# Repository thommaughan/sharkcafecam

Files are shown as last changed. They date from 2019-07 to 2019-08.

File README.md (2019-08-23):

# sharkcafecam
SharkCafe Cam - white shark camera tag with behavior detection triggered video

### How to navigate this repository
First of all, welcome to Shark Cafe Camera. The first thing that you will need to review is the "ToolList.md" file. This will provide you with the necessary tools and optional tools that will assist you with completing this project. Each tool is listed as the name of the tool, cost, and a blue hyperlink text which will take you the the website to order that tool. Tools that are listed as optional are not necessary for the project but can provide some ease with certain aspects. The tools listed as none optional were chosen as ideal due to the fact that you can go to your local hardware store and purchase these tools and they are the relatively cheaper versions. These are not the specific tools we used for this project but are merely recommendations. Feel free to find, borrow, or use other tools that will accomplish the same tasks.

The next step if you are not familiar with soldering should be to review the "SolderingBasics.md". This will provide you a brief overview of soldering tools and techniques that will assist you with this project. Feel free to also research other resources for example you tube videos or manuals as these can provide more detailed information about this topic.

After you have completed the first two sections or you are familiar with soldering then you are ready to navigation the rest of this repository. The organization of this reprository is as follows. Each folder describes a certain component of the overall project. The subfolders within each of these folders has  a combination of subfolder including a readme.md, mechanical, electrical, and software. First, you should open the "readme.md" which provides necessary information or steps for that component. The Mechanical describes any physical component or mechanism for that component. The electrical describes the components used and how the were wired. The software describes any software that was used to control the electrical components. 

Use these materials as guidelines to further experiment with other cameras or devices. This is merely to show how this project was accomplished and the potential possibilities. 

If you have any questions or any part of these materials are confusion, please feel free to leave comments on sections that are confusing. 

Have fun and go exploring with your new remote sensing camera!

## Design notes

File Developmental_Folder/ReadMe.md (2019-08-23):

## Developmental Files for Repository

This folder stores the necessary developmental files for this repository. These are files used in other parts of the respository for examples pictures used in the SolderingBasics Tutorial.

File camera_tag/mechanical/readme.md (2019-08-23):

## Camera Housing

  The files associated with the mechanical describe the camera housing with use of the HDR-AZ1 Sony Action camera which is unfortunately no longer in production. The "A-201898-17.PDF" shows the whole assembly with the sony cammera and batteries in place.
  "P-201897-17_SonyMold" files show the PDF view of the 3-D printed assembly housing the camera and the batteries. The other files by the same name are SolidWork files and Projects. "P-201900-17_AcrylicLens" files which were custom machined on site at the Monterey Bay Aquarium Research Institute (Double Check this).
  The "Sony Batteries" are solidworks drawings and files used with association of the "A-201898-17.PDF" as visual indicators of how the batteries are positioned in the housing. 

## How to use these files

As stated before, these files were created using the Solid Works Software which is linked below. This is a professional software platform that is used widely in many industries. A key take away from these files are to have a visual of how this version of this shark cafe camera was assembled. If you have 3-D manipulation/drafting experience, feel free use these files to create your own housing. 

[Solid Works Software](https://www.solidworks.com)

Below is a link to a 3D printing services. This is merely an example of one company. The parts for the camera housing were printed in house at the Monterey Bay Aquarium Research Institute. Use this link below as merely an example of the 3D printing services and research other alternatives if you decide to use this model. 

[3 Space Printing Service](https://3space.com/3d-printing-ppc?gclid=CjwKCAjw1_PqBRBIEiwA71rmte2ELk5xJ86E6CFk6ArePkv97ztjzFWGFQ25XP00T4se_XzOaefN1xoC2_sQAvD_BwE)

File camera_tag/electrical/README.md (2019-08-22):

# Shark Cafe Cam Main Board Information
## Files
#### 1. Schematic
#### 2. Board design
## Internal components

#### 1. Processor
#### 2. Sensors  
   Note: We show breakout boards for the sensors to show that these can be bought seperately, utilized individually, and have code and tutrials available by their manufacturers online. On the board these sensors are cut down to the essentials to make for a more compact design.
#### 3. Camera trigger
```
Note on camera trigger transistors: they allow for switching the camera on/off and record/stop. These transistors work by allowing current to flow through the camera when they are triggered. In a way they act as an electrical switch, when power is sent to them you're flipping the switch 'on', thus activating the camera, when no power is sent, the switch is flipped 'off' and the camera disactivates.
```

### Processor

| Part         | Function          | Board Code    | Description       | Link and part number      |
| --------------------|:-------------:|:-------------:|-----------------|----------------- |
|  | Processor | N/A | Central processing. Same processor found in Feather M0, can be accessed as such through Arduino IDE.| ATSAMD21G18A |

boardforedit

### Sensors (included)

| Part breakout board         | Function          | Board Code    | Description       | Link and part number      |
| --------------------|:-------------:|:-------------:|-----------------|:---------------------------:|
|   | RGB sensor  | U1  | Red, green, blue light sensor  |  [ISL29125](https://www.sparkfun.com/products/12829)   |
|   | IMU        | U4           | Accelerometer, gyroscope, and compass | [MPU-9250](https://www.invensense.com/products/motion-tracking/9-axis/mpu-9250/)   |
|   | Capacitive sensing         |   U6   | 4 Channel Capacitance to Digital Converter  | [FDC1004](http://www.ti.com/product/FDC1004)  |

### Trigger (for camera or other device. Transistor.)

| Location on board         | Function          | Board Code    | Description       | Link and part number      |
| --------------------|:-------------:| -------------|-----------------|---------------------------|
| Cam Trigger  |  2 FETs, one turns the camera on/off and the other records/stops.  | CAM1  | Trigger for camera. R and P are transistor drains, G is the common source.  |  [Transistors](https://learn.sparkfun.com/tutorials/transistors/all#extending-the-water-analogy)   |

### Electrical components

| Part Number/Name         | Function          | Board Code    | Description       | Link       |
|:--------------------:|:-------------:|:-------------:|:-----------------:|:-----------------:|
| SN74LVC2G66DCUR  | Switch         | U5    | Dual Bilateral Analog Switch  | [SN74LVC2G66DCUR](http://www.ti.com/lit/ds/symlink/sn74lvc2g66.pdf)  |
| TPS22918            | Load Switch         | U8     | Details in datasheet  | [TPS22918](http://www.ti.com/product/TPS22918)  |
| 2N7002BKS           | MOSFET         | Q1     | Transistor drain  | [2N7002BKS](https://assets.nexperia.com/documents/data-sheet/2N7002BKS.pdf)  |
| ZXCT1109            | Current sense monitor         |   U9   | Details in datasheet  | [ZXCT1109](https://www.diodes.com/assets/Datasheets/ZXCT1107_10.pdf)  |
| TPS78033            | LDO regulator         | U7     | Details in datasheet  | [TPS78033](https://www.findchips.com/detail/tps78033/2477-Texas%20Instruments?quantity=1)  |
| MCP73831            | Charge Management controller         |  U3    | Details in datasheet  | [MCP73831](https://cdn.sparkfun.com/assets/learn_tutorials/6/9/5/MCP738312.pdf)  |
| Direct wire uSD connect        | Micro SD card connector         |   J9   | Pins for soldering MicroSD card on.  | N/A  |
| USB-MICROB 5v                | Data transfer and power with computer         | J6     | Micro USB connector port  | N/A  |
   
 ### *For information on how to communicate with the board and each sensor, check out the software section.*

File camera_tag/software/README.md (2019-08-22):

For what's available on the board, navigate to [**camera_tag/electrical**](https://github.com/thommaughan/sharkcafecam/tree/master/camera_tag/electrical).

To get started with coding, head to [**software/Getting_started(+how_to_program)**](https://github.com/thommaughan/sharkcafecam/blob/master/camera_tag/software/Getting_started(%2Bhow_to_program).md).

boardforedit  
The purpose of using the same processor as the Feather M0 is so that you can communicate with this board through the Arduino IDE as you would with the M0. In other words, installing the drivers for the M0 will allow you to communicate with the main board for the camera tag.

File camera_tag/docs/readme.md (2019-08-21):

## READ ME

Each of these subfolders contains different aspects of this particular component. In this case, these folders relate to the camera, the board controlling the camera and sensor components, and the housing which contains all of these aspects. Please read each "readme" file to understand in more detail the types of files and their purpose. 

In the electrical file, there is a list of the sensor that are embedded in the board and what their function is. This also contains the layout of the board and design files. 

The mechanical file contains files related to the 3-D printed housing. 

Software contains some example codes that control different sensors of the board.

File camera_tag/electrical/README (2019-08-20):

# Shark Cafe Cam Main Board Information
## Index
1. Schematic
2. Board design
#### Internal
1. Processor
2. Sensors
| Part Number   | Name          | Board Code    | Description       |
| ------------- |:-------------:| -------------:|----------------:  |
| ISL29125            | Record        | D4_IO_PWR     | Transistor drain  |
| MPU-9250             | Ground        | N/A           | Transistor Source |
| FDC1004             | Power         | D9_IO_REC     | Transistor drain  |
| SN74             | Power         | D9_IO_REC     | Transistor drain  |
| FDC1004             | Power         | D9_IO_REC     | Transistor drain  |
| FDC1004             | Power         | D9_IO_REC     | Transistor drain  |
| FDC1004             | Power         | D9_IO_REC     | Transistor drain  |
| FDC1004             | Power         | D9_IO_REC     | Transistor drain  |
   
 For information on how to communicate with the board and each sensor, check out the software section

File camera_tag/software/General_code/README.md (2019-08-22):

### This sketch (Arduino program) contains tidbits of code for a variety of board uses.  

**Note:** Make sure to either download the necessary libraries (anything that says **#include <libraryname.h>**) or comment them out (add **//** before).  

**Note:** a piece of code needs to be added to the SD card reading lines so that the information syncs or writes. As is, empty files are being written to the SD card and once that number reaches 100 the code will stop working. ALternatively, comment out that portion.

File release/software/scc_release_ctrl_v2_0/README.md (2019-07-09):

msp430_i2cEEPROM
================

Skeleton framework for reading and writing from a  24AAxx I2C EEPROM chip for MSP430 Launchpad/MSP430g2553

Pinout for the launchpad - P1.6 = SCL; P1.7 = SDA

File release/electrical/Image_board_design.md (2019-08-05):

Board Design
-------------

<p align = 'center'>Designed by Thom Maughan</p>
<p align = 'center'><i>Eagle</i> file can be found within <b>scc_release_v2_3.zip</b></p>

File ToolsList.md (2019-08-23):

## Tools List

1. Aven Soldering/Desoldering kit: $29.52 - [Soldering Iron Kit: HomeDepot](https://www.homedepot.com/p/Aven-Soldering-Desoldering-Kit-7-Piece-17502/206311913)
2. Precision Wire Strippers AWG 20-10: $4.72 - [Wire Stripper: HomeDepot](https://www.homedepot.com/p/Pro-sKit-Precision-Wire-Stripper-AWG-20-10-CP-302G/206679687)
3. 28AWG Stranded Wire Kit: $14.99 - [Hook Up Wire: Amazaon](https://www.amazon.com/Electrical-different-Insulated-Temperature-Resistance/dp/B07G2HFCS1/ref=asc_df_B07G2HFCS1/?tag=hyprod-20&linkCode=df0&hvadid=242022044358&hvpos=1o2&hvnetw=g&hvrand=15746777807985423264&hvpone=&hvptwo=&hvqmt=&hvdev=c&hvdvcmdl=&hvlocint=&hvlocphy=9032735&hvtargid=aud-801381245258:pla-522539120773&psc=1)
4. (Optional) 3.5in. 2X Helping Hand with Magnifer: $12.52 - [Helping Hand Stand: HomeDepot](https://www.homedepot.com/p/Stalwart-3-5-in-2X-Helping-Hand-Magnifier-with-Stand-75-KS508/206362835
5. (Optional) High Temp Hot Glue Gun: $5.99 - [Hot Glue Gun: Amazon](https://www.amazon.com/Electrical-different-Insulated-Temperature-Resistance/dp/B07G2HFCS1/ref=asc_df_B07G2HFCS1/?tag=hyprod-20&linkCode=df0&hvadid=242022044358&hvpos=1o2&hvnetw=g&hvrand=15746777807985423264&hvpone=&hvptwo=&hvqmt=&hvdev=c&hvdvcmdl=&hvlocint=&hvlocphy=9032735&hvtargid=aud-801381245258:pla-522539120773&psc=1)

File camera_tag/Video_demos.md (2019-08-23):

Youtube demonstrations of the camera tag in action
==================================

### Youtube video of the camera tag being triggered to turn on and record by the onboard inertial measurement unit.
IMU_triggering (https://www.youtube.com/watch?v=_-qGrMnmp10&feature=youtu.be)

https://www.youtube.com/watch?v=_-qGrMnmp10&feature=youtu.be

### Youtube video of a camera being triggered to turn on using the red-green-blue light sensor on the main board.
RGB_triggering (https://www.youtube.com/watch?v=f3s8aPaXeHw&feature=youtu.be)

https://www.youtube.com/watch?v=f3s8aPaXeHw

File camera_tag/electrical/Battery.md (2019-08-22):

How to prepare a battery for your board
=========================================

*The brown cable in this setup is ground*


*Make sure the positive and negative terminals of your battery are connected to the white connecter in line with how the board's positive and negative terminal are aligned. We had to switch the wires on the battery. To do this, follow this simple guide:*
HTB1UNq4OXXXXXbNXpXXq6xXFXXXk



When connecting a battery make sure the wires are in the correct orientation within their housing. Make sure you connect the ground wire to the ground pin and the power wire to the power pin on the battery, reference the board design file to make sure.

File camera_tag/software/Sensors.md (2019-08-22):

# Access sensors on the board
In an effort to teach you how to access *any* sensor on the board, we will offer detailed instructions for a simple sensor and a more complex one. For the rest, the part number and library will be provided. The idea is that you'll follow the same procedure with the rest of the sensors as you did with the two provided. The purpose of this is to get you comfortable with navigating the code necessary to utilize these sensors in any way you please. If you already feel comfortable navigating code, feel free to download the sample code directly (camera_tag/software/sample_code).  

Sensor Libraries  
To facilitate communication with a sensor you can download a library.
```
Note: A library is a compilation of functions for a specific module or sensor. It allows for facilitated control of a device by offering the code to control it in more easily understood snippets. You can tell a library is being used if you see: #include <libraryname.h> at the top of the program. To figure out what functions are available in the library you can look up the library name online or look through its folder you downloaded.
```  
### Red Green Blue (RGB) sensor (ISL29125)
RGB
1. Download the **SFE_ISL29125** folder from */Libraries.*
2. Move the folder into your computer **Documents** > **Arduino** > **libraries**. Make sure both the .h and .cpp files are in the folder you're adding.
3. Restart your Arduino IDE.
4. On the IDE select **File** > **Examples** > **SFE_ISL29125** > **ISL29125_basics**
5. Run the code
   1. Open the serial monitor (ctrl+shift+m) to view the RGB sensor readings.  
   Note: if you want the readings as decimal values change 'HEX' to 'DEC' in the code.
   
### Inertial Measurement Unit (IMU) (MPU-9250)
MPU
1. Download the **SparkFun_MPU-9250** folder from */Libraries.*
2. Move the folder into your computer **Documents** > **Arduino** > **libraries**. Make sure both the .h and .cpp files are in the folder you're adding. Check the src folder within.
3. Restart your Arduino IDE.
4. Download the **IMU_code** sketch from */software.*
5. Run **IMU_code** to receive IMU measurement values.
   1. Open the serial monitor (ctrl+shift+m) to view the sensor readings.

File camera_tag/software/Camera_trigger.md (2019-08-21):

# Camera Trigger
### 1. What is it/how does it work
### 2. How to use it

Cam Trigger

| Symbol        | Meaning       | Name on Code  | Pin       | What is it?       |
| ------------- |:-------------:| -------------:|-------------:|----------------:  |
| R             | Record        | D4_IO_PWR     | 4  |Transistor drain  |
| G             | Ground        | N/A           | N/A |Transistor source  |
| P             | Power         | D9_IO_REC     | 9  |Transistor drain  |

### 1. What is the trigger?  
   The triggers (there are two) are two logic level field effect transistors (FETs) that share the same source (ground). A transistor acts like a switch that you flip with a command instead of with your finger. This allows you to 'flip' on/off any device connected to the trigger. *Logic level* is in reference to the amount of power required to flip the switch. A logic level transistor can be 'flipped' with less voltage, such as what a microcontroller like this board can provide. Instructions on how to prepare a device for this sort of triggering are found in **camera_tag/electrical/camera_prep.**  
   
### 2. How to use the onboard triggers 
   To trigger the transistor you need to output power to either pin 4 or 9 depending on which you want to use (they both work). In some of the example code provided these pins are defined as either D4-IO_PWR or D9_IO_REC. There is example code provided in **camera_tag/software/trigger_code.**

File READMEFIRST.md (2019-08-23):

# Shark Café Cam

### How to navigate this repository
Each folder describes a certain component of the overall project. The subfolders within each of these folders has  a combination of subfolder including a readme.md, mechanical, electrical, and software. First, you should open the "readme.md" which provides necessary information or steps for that component. The Mechanical describes any physical component or mechanism for that component. The electrical describes the components used and how the were wired. The software describes any software that was used to control the electrical components. 

The first two folders to open are the tools list and soldering basics. The tools list describes all necessary tools to work with or create the necessary components of this project. Soldering Basics describes the process of soldering and some tips that may help with completing or ensuring the stability of components. 

### Goal
The goal of this open source guide is to enable people to build their own behavior triggered animal cameras that they can utilize for their own projects and purposes. This open source is built with the mindset that It has enough information to where it can stand alone, yet benefits from further investigation.

### Behavior triggered camera tag
The shark Cafe Cam is a behavior-triggered imaging system that was developed by MBARI engineers to study the behavior of white sharks (*Carcharodon carcharias*) during their stay in the north pacific. This system is intended to be modular, with the ability to be built from different components granted modification extends to the rest of the system. The purpose of these instructions is to allow someone to build a shark-mounted camera themselves. To learn what components are needed and how they’re put together and prepared. This system is intended to be low cost, light weight, retrievable and reusable.

### The Shark Café
journal pone 0047819 g002
<p align = 'center'>Position estimation of White Sharks. Each dot represents where a White Shark is estimated to have been. <a href="https://journals.plos.org/plosone/article?id=10.1371/journal.pone.0047819">(Jorgensen, et al. 2012)</a></p>

For a long time little was known of white shark migration. They were thought to stay around the California coast. In 2012 Sal Jorgensen and his team tracked a group of white sharks and found out the reality was more mysterious. The image above shows estimated migration routes of white sharks with ech dot representing a location estimate for a given time.The large cluster of dots in the center of the above image shows that white sharks are staying in that area between the coast of California and Hawaii. This puzzled scientists. The area, for its mystery, and yearly congregation of white sharks was named the White Shark Café.

### The Team


pic edit

### History (Timeline)
include iterations leading up to newest design

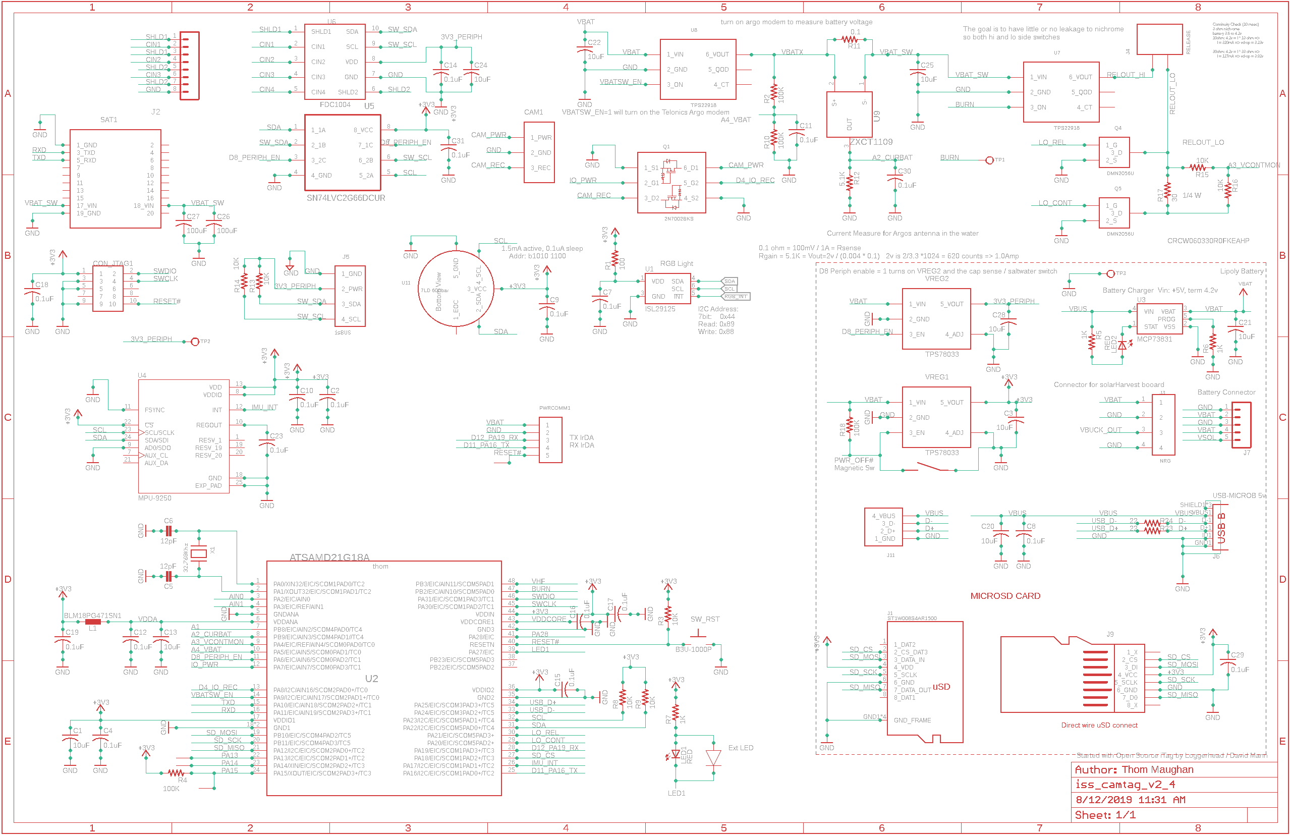
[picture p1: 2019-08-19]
camera_tag/electrical/Schematic.png

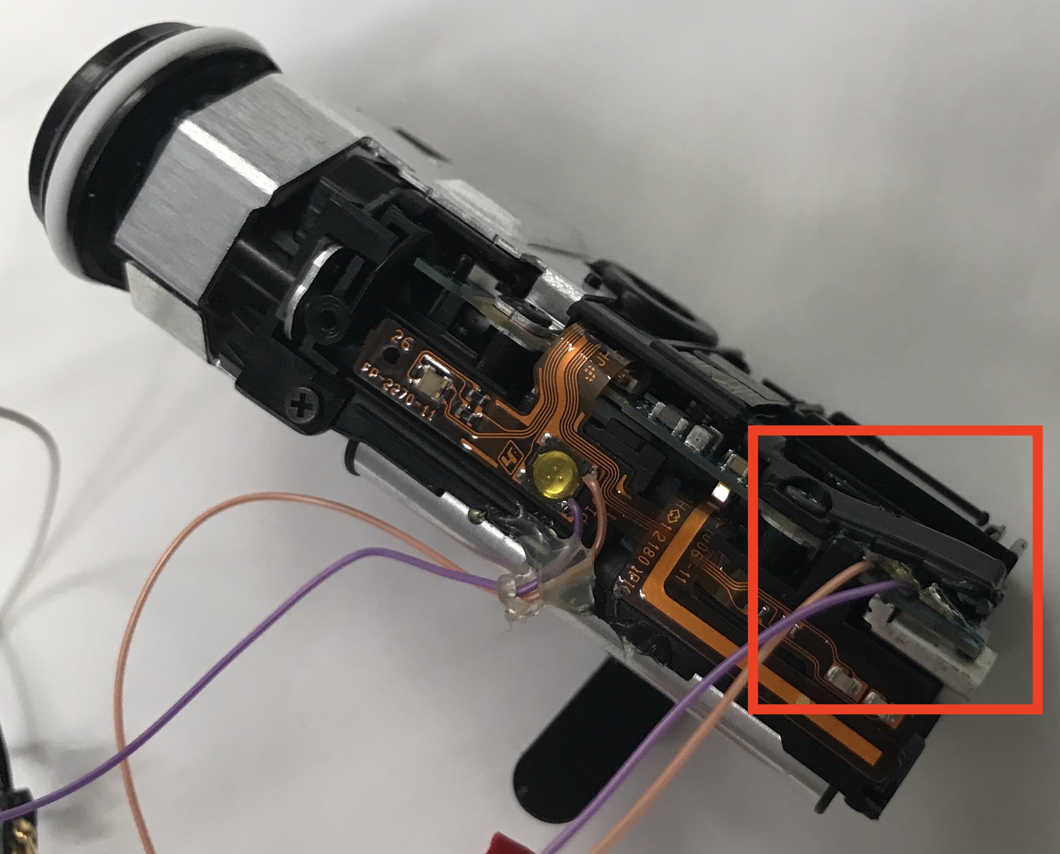
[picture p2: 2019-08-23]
Developmental_Folder/Hot_Glue_Camera_2.jpg

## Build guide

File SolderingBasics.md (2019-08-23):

# IMPORTNAT MESSAGE: IT IS VERY IMPORTANT TO SODLER IN A WELL VENTILATED AREA AND TO KNOW WHERE YOUR SOLDERING IRON IS WHILE IT IS ON AND HOT. THIS IS A VERY HOT TOOL SO PLEASE BE CAREFUL WHEN PLACING IT DOWN AND MAKE SURE THAT YOU DO NOT TOUCH THE TIP OF THE SOLDERING IRON OR ANY SURFACE AS IT WILL CAUSE ITEMS TO BURN

# Soldering Basics
This tutorial is for first time beginners to understand soldering practices, techniques, and procedures. Soldering is the practice
of melting soldering to create a strong conductive connetion between components. Solder is an alloy that can be either lead based or
lead free. Each type has a different type of chemical composition. Listed below are some of the tools used in soldering and their
purpose. The images shown below are the tools that were used to create some of the components. These tools pictured are different than those show in the "ToolList". 

# TABLE OF CONTENTS
## 1. Soldering Tools
## 2. Cleaning the Soldering Iron
## 3. Removing Soldering
## 4. Soldering two wires together (Tinning Technique)
## 5. Soldering Wires to Components
## 6. Tips and Tricks

### 1. Soldering Tools

#### Soldering Iron
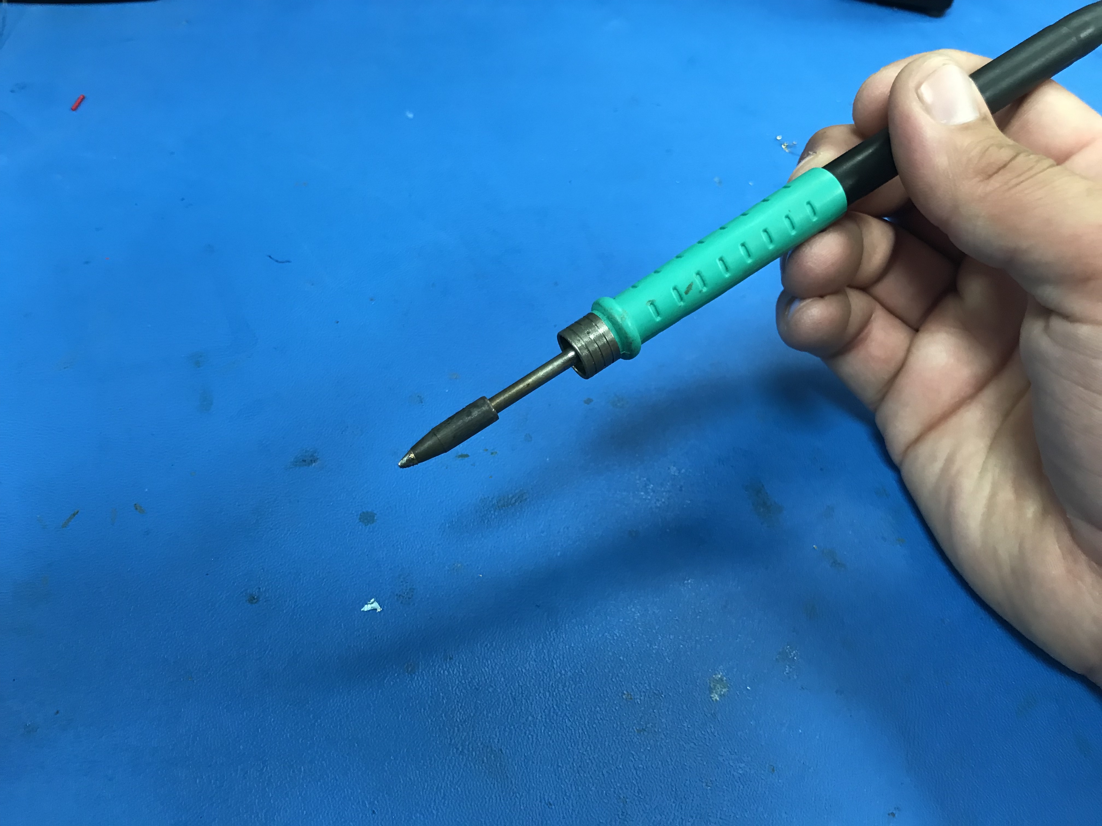
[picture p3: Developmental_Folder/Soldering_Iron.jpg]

This is the heated element that melts the solder. The tip of this tool becomes extremely hot so please make sure that you know where this tool is at all times and be very careful when handling. Most times, these tools will come with some type of holder that will allow you to 
store this tool while it is hot. 

#### Soldering
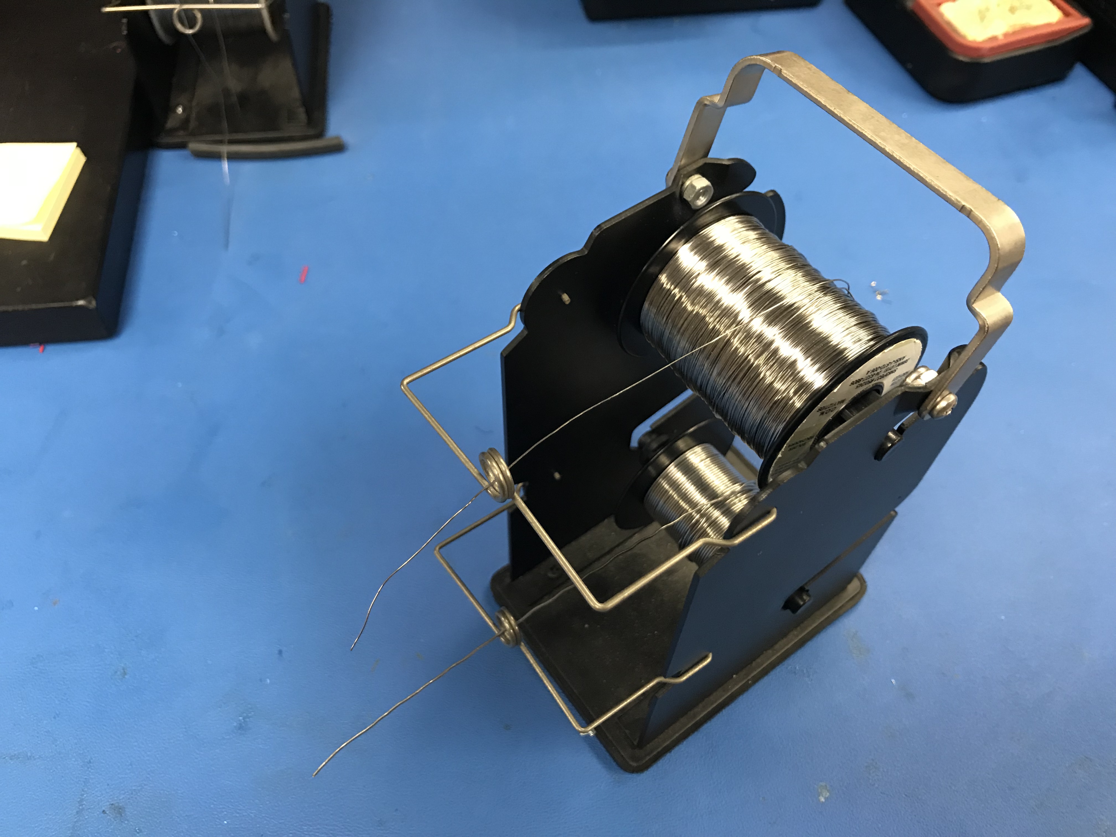
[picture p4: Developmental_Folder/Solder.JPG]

This image shows soldering that is set up in holder. Soldering comes in varying thickness.

#### Soldering Station
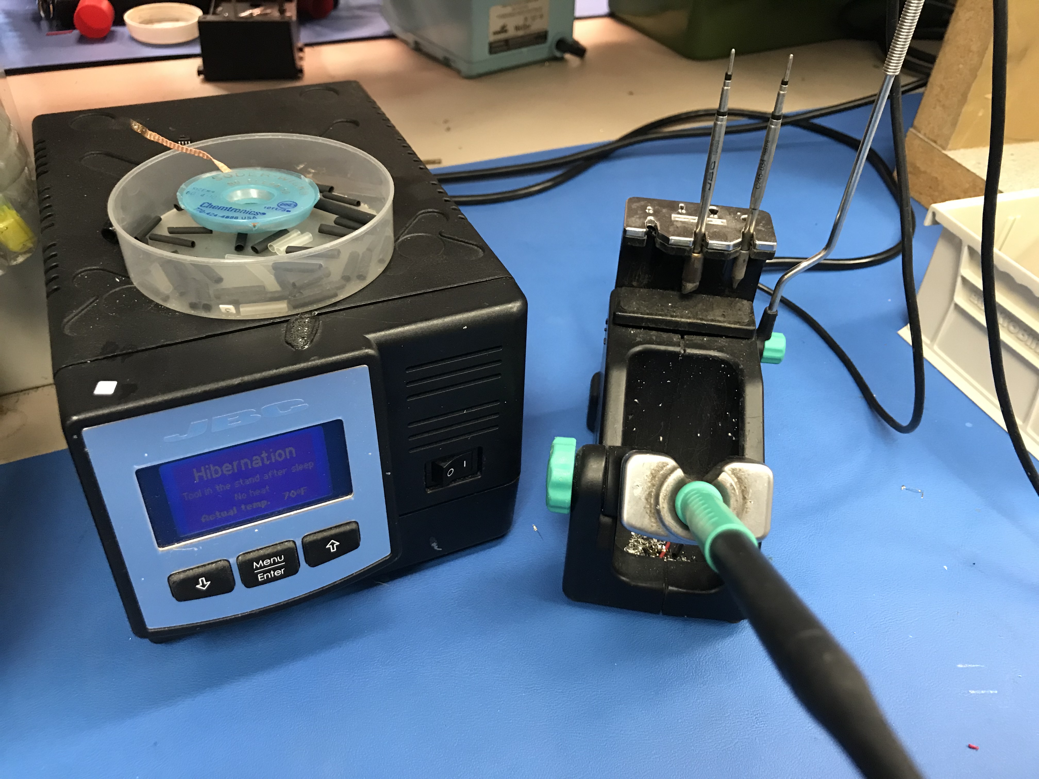
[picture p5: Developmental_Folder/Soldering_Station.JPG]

Some Soldering Irons come with a soldering station while others may not. A soldering station usually controls the temperature of the soldering iron and also provides a stand which to place the soldering when not in use.

#### Soldering cleaning station featuring brush wire and sponge
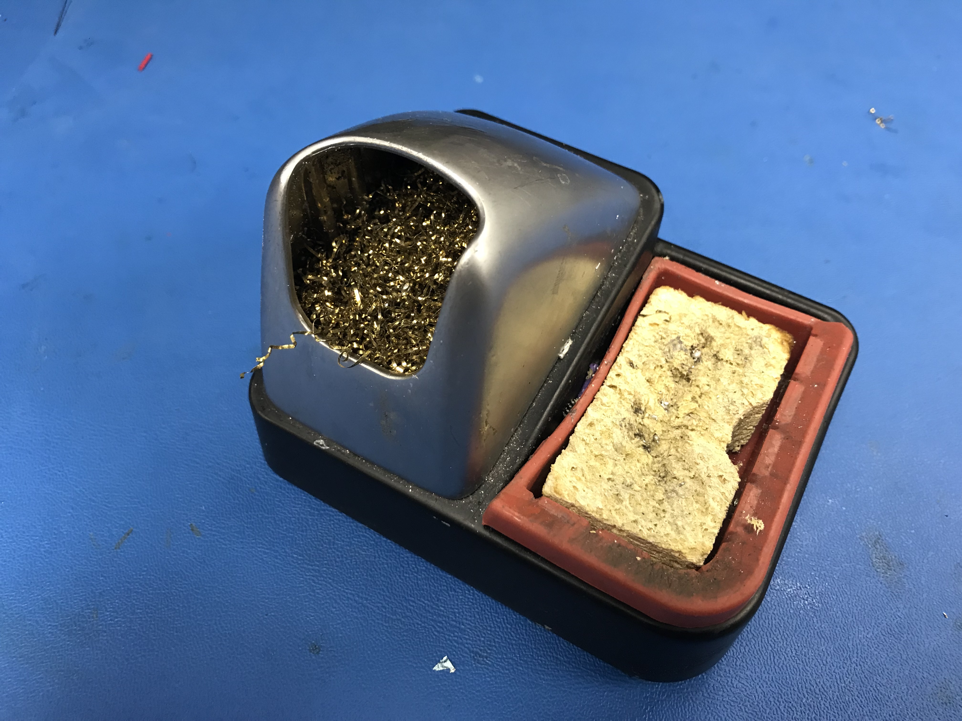
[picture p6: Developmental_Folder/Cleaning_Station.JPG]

This cleaning station removes oxidized soldering which you should do each time before you make a new electrical connection. This features two different types of cleaning techniques. One is the wire brush and the other is a wet sponge. Both will be explained later in this tutorial.

#### Wire Strippers

This tools removes the plastic jacket that covers most wires. There are a series of cutting size that match the gauge of the wire. This will allow you to cut through the plastic jacket without cutting through the wire. 

#### Soldering Wick
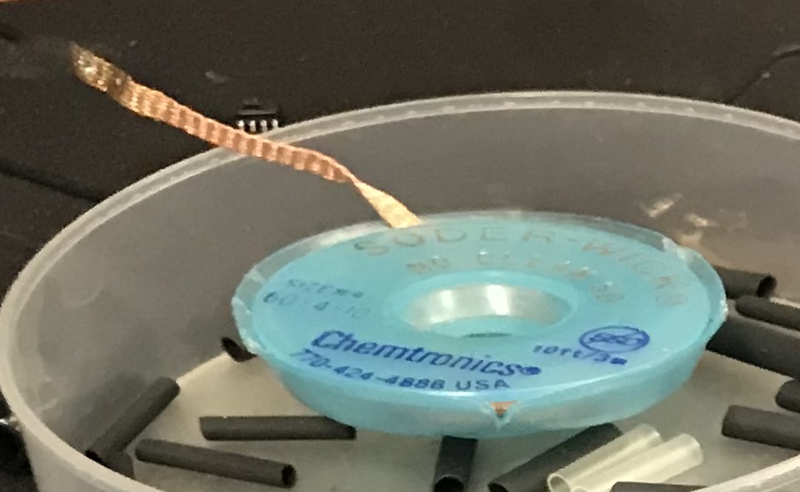
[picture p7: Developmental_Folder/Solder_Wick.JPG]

This is used to remove solder from connections or electrical components. How to use this is described below the "Cleaning the Soldering Iron" Section. 

## 2. Cleaning the Soldering Iron
As you read through the following steps you will need to periodically clean the oxidized solder off of the tip or your soldering iron. With out cleaning station we have both a wire brush and a wet sponge. With the wire brush, merely scrape the end of the tip against the wire brush as shown below. With the wet sponge, drag the tip against the wet sponge to remove the old solder. It is important that the sponge is wet. 
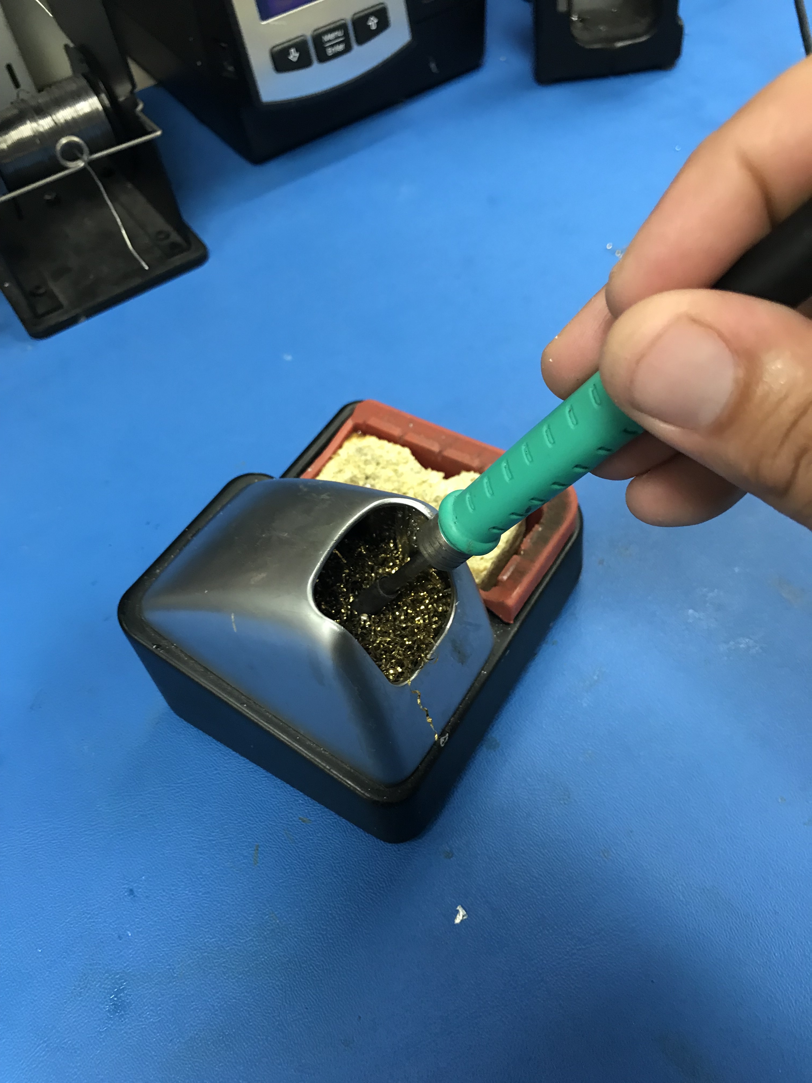
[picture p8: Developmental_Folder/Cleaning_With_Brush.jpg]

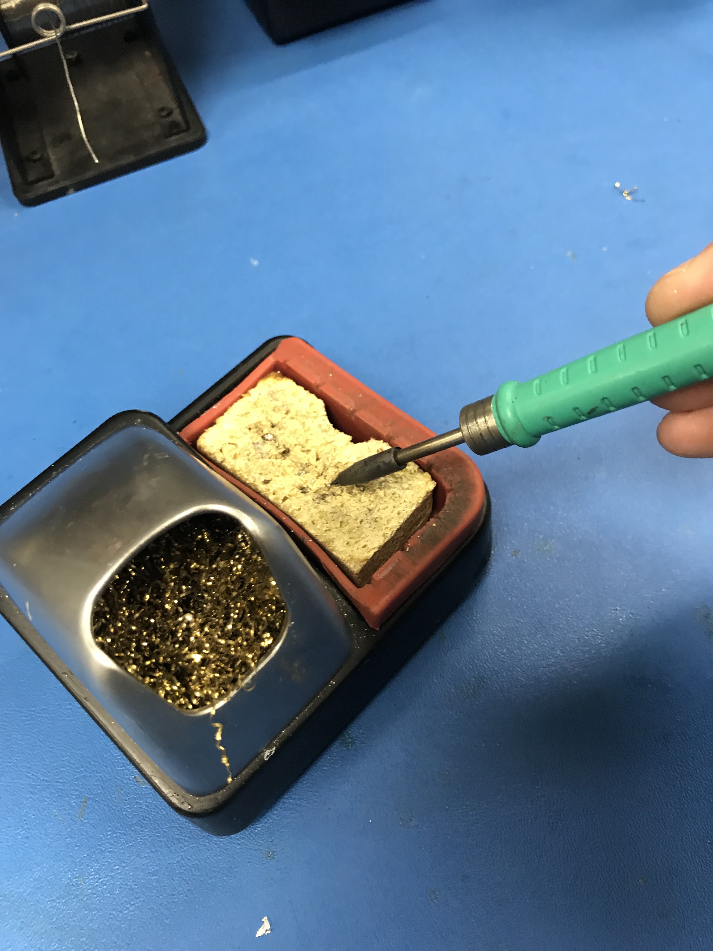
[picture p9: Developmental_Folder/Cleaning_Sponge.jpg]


## 3. Removing Solder
Below we describe how to use the soldering wick but if you purchase the soldering kit from our ToolList it comes with a manual desoldering pump. the following link shows a video on how to use this device and also more detail about using Soldering Wick.
[Desoldering Techniques](https://www.youtube.com/watch?v=Z38WsZFmq8E)

To use the Soldering Wick place the soldering wick between the connection you wish to remove and the soldering iron tip as shown below. This will cause the soldering to move from the connection to the soldering wick or soldering iron. After that section of wick is encompassed in solder, cut this section and dispose of. 
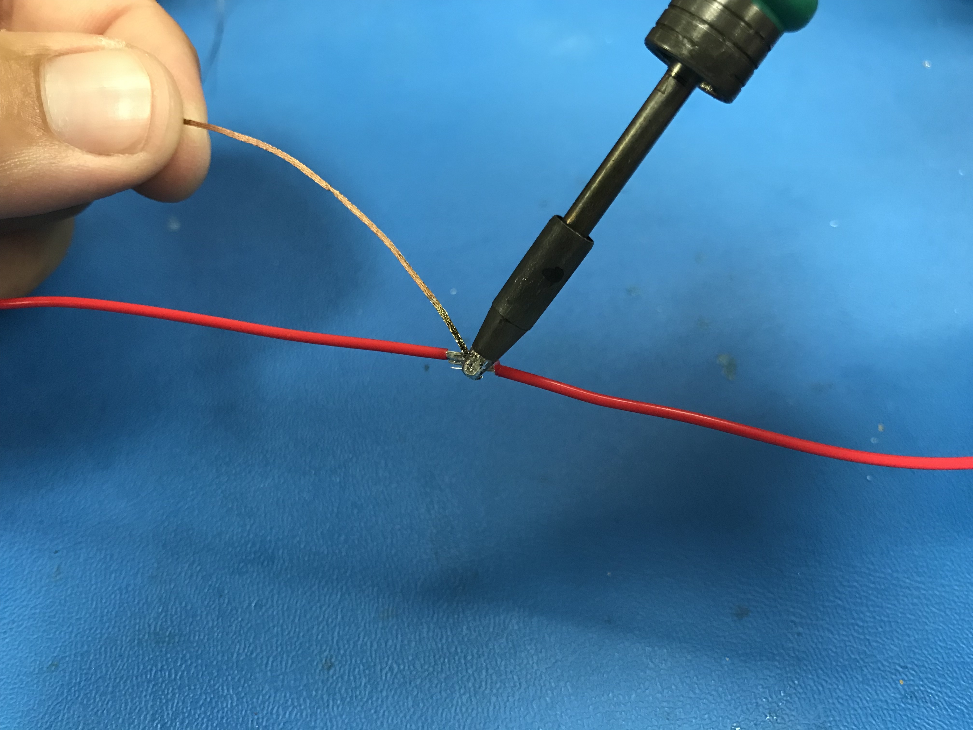
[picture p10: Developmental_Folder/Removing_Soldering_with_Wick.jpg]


## 4. Soldering two wires together (Tinning Technique)
This first part will describe how to connect two wires together. This will require you to tin both wires and then melt them together to create the electrical contact. 

#### Step 1: Stripping the wires
Hold the wire about an 1/8th of and inch from the end of each wire and place the wires strippers around the corresponding wire size. You will need to go a few size up meaning that if you are using a 22AWG (American Wire Gauges) then you will most likely use the 24 or 26 size cutting surface. Squeeze the wires cutters just as you would squeeze a pair of scissors and gently move the wire strippers away from the wire. 
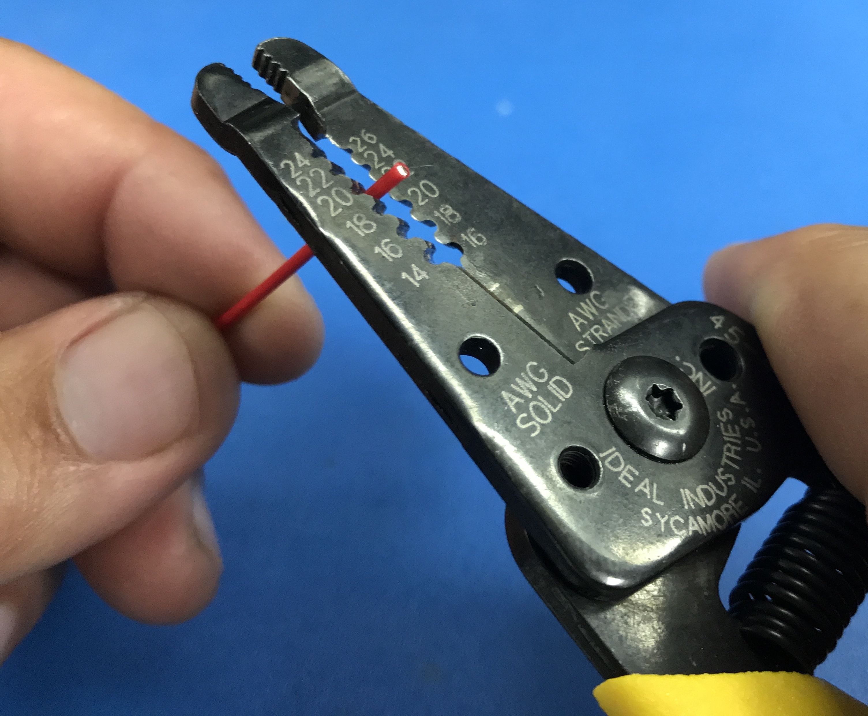
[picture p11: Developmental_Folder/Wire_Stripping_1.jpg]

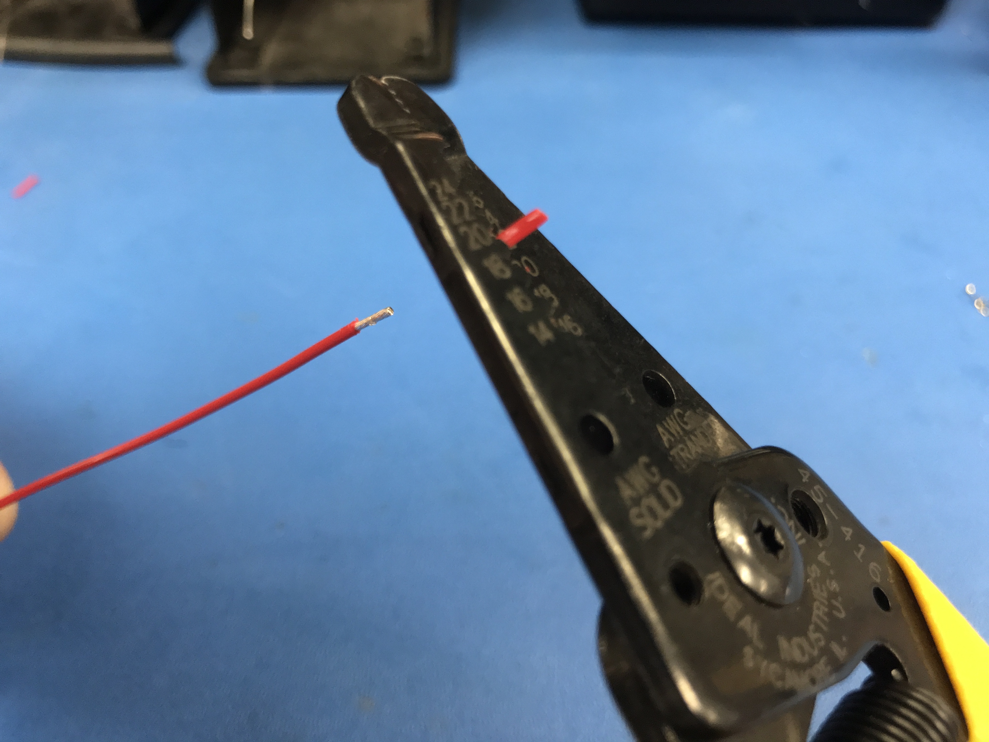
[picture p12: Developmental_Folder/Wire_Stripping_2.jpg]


#### Step 2: Setting up the Soldering Iron/ Soldering Iron Station
Make sure that the soldering iron is in it's holder and follow the instructions provided by the manufacture if you purchased that soldering iron. 

#### Step 3: Priming the Soldering Iron
Once the soldering Iron is hot and ready for you you will need to prime the time. You perform this task by melting a small amount of soldering onto the soldering iron tip. Only hold this for about 2 to 3 seconds and make sure that is a not a large blob. 
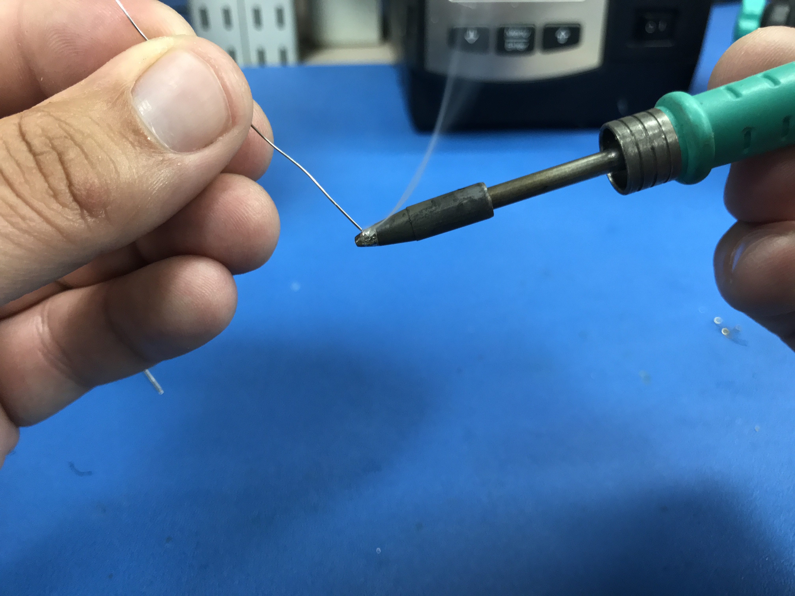
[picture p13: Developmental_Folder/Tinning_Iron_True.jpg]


#### Step 4: Tinning each of the wires
If you have purchased the third hand then that device will come in very useful however, it is not necessary. After priming the soldering iron tip, tin the two wires by holding the tip against the exposed wires and placing the solderin opposite of the soldering iron. This will cause the soldering to melt through wire. 
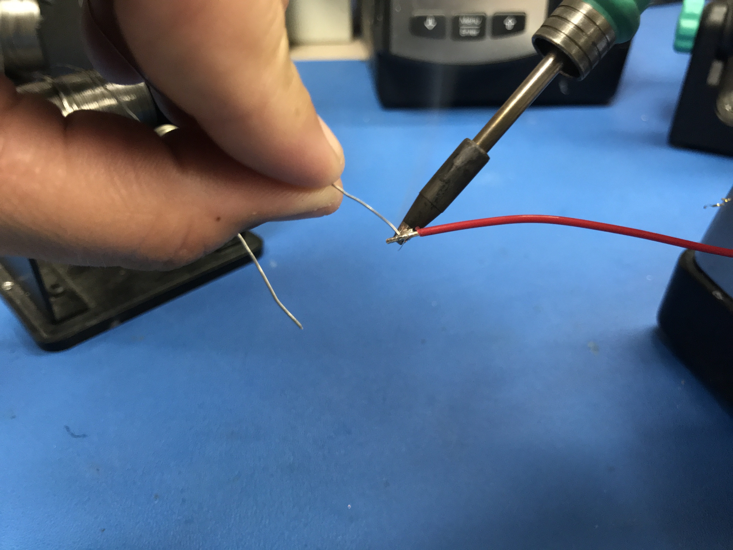
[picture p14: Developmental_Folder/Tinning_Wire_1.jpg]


#### Step 5: Soldering wires together
Again using either the third hand or other clamping device, hold both tinned ends of the wires together as shown. Then press the soldering iron to this joint holding for only about 2 to 3 seconds or until you visible see that the solder has melted and has created a connection between the two wires. 
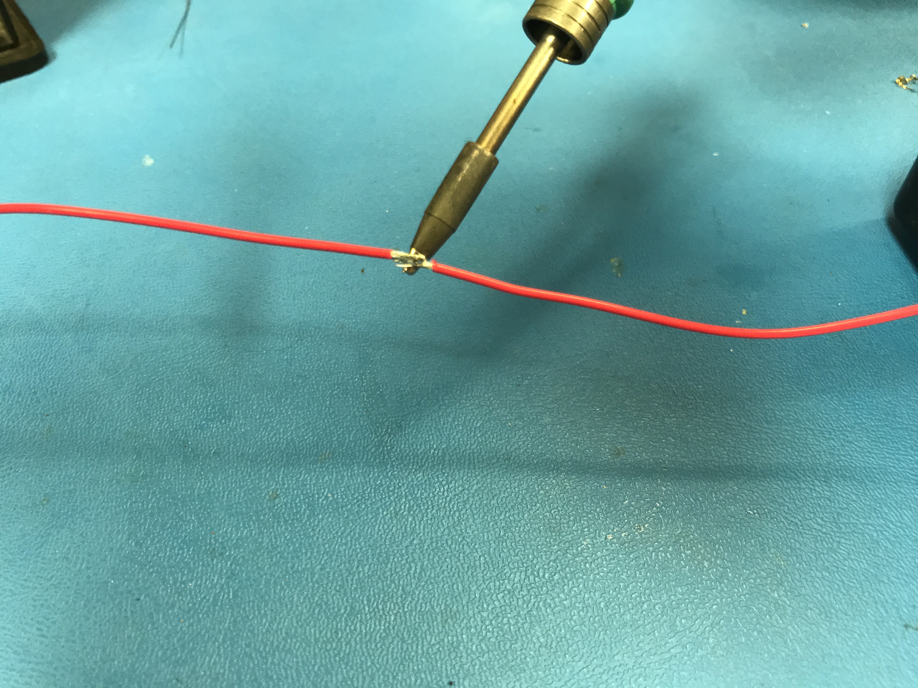
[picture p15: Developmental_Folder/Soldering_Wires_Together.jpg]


At this point it is a good practice to cover this joint with electrical tape or liquid electrical tape. These both can be found at your local hardware store. This reason bein that these are exposed wires that if crossed with other exposed wires may create an electrical short and destroy components. There are proper techniques to cover these for example the use of heat shrink which I have attached a hyperlink below to a you tube video showing the process. However, it is not necessary for the steps in this project. 

[How to use Heat Shrink](https://www.youtube.com/watch?v=LD9kBax1DDk)

## 5. Soldering Wires to Components
This section merely shows a quick example of how to solder wires to electrical components. First of all, prime your soldering iron, strip your wire and tin the exposed wire. Next hold the tinned wire to the spot which you would like to solder your wire. Next hold the soldering iron to the tinned wire and the metal contact section that you would like to solder to. The pictures below show two wires being soldering to opposing terminals of what was once contacting a switch. Do not hold the soldering wire for long peroids of times agains electronical components. These components maybe sensitive to heat so 2 to 3 seconds preferable time scale as to not over heat components.
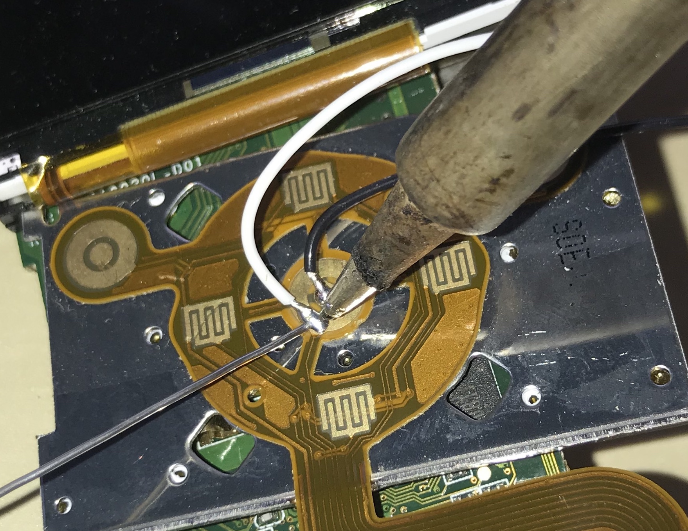
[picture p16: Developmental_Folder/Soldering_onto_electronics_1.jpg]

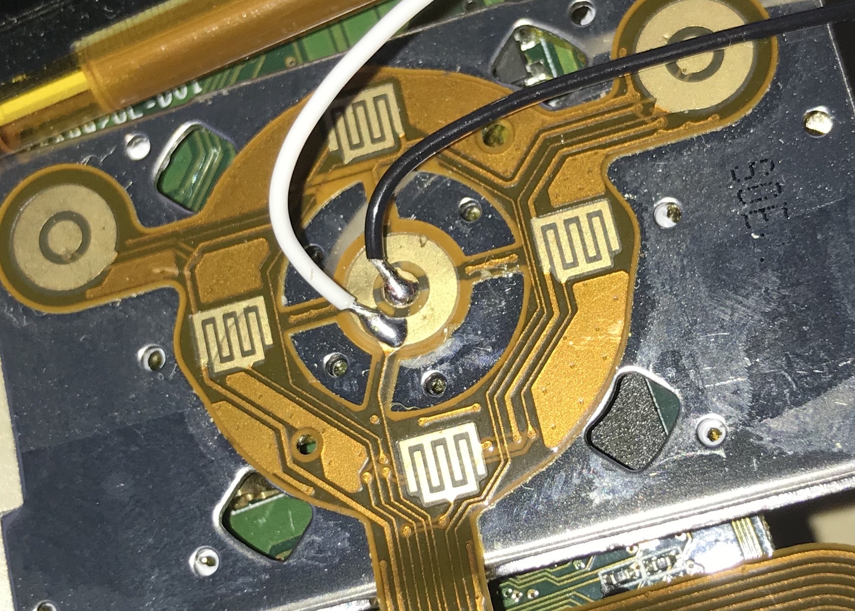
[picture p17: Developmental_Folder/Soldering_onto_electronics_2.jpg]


## 6. Tips and Tricks
After you solder wires to certain components it maybe helpful (and if you have the option) to apply some hot glue to hold down the wires to the component. This is shown by the red box. HOWEVER, DO NOT USE THE HOT GLUE ON THE FLEX WIRES WHICH SOME EXAMPLES ARE OUTLINED BY THE VIOLET BOXES. THE REASON BEING, THE HOT GLUE WILL MELT THESE WIRES. 
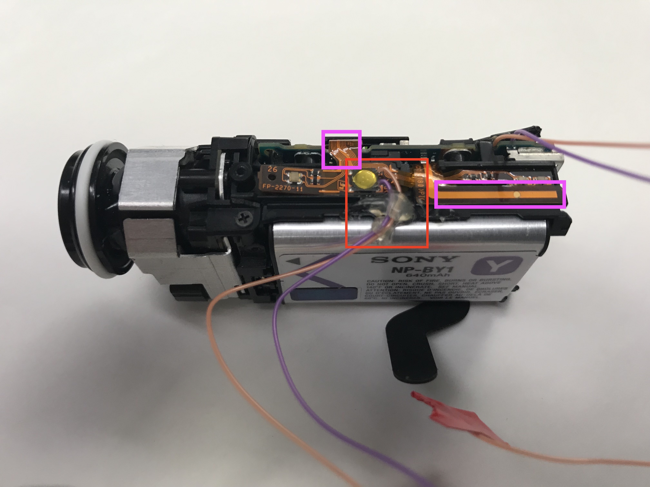
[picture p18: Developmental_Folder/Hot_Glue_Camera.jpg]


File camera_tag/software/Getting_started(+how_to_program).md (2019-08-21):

# Getting started with the board

*The word 'communicate' is used in this guide as: exchange of information between you and your board. Succesful communication allows for full manipulation of the board and its components, whether gathering information, switching on/off, etc.*

### Materials: Computer, microcontroller (main board), USB to micro-USB cable.
### Objective: Communicate with your microcontroller and have it respond to test for succesful communication.

 *In an effort to get straight to programing the board we will offer a condensed version of getting started with the Arduino integrated development environment (IDE). The Arduino IDE is a platform created by Arduino to interface with a variety of microcontrollers.*

#### Step 1: Download the Arduino IDE
Go to [Arduino Main Page](https://www.arduino.cc/en/main/software) and scroll down to:

Select the appropriate download for your system and follow the instructions.

#### Step 2: How to get set up (downloading the necessary drivers)
https://learn.adafruit.com/adafruit-feather-m0-adalogger/setup
There’s two important pages in the Adafruit instructions ‘Arduino IDE setup’ and ‘Using with Arduino IDE’. Follow the first ‘Arduino IDE setup’, download the arduino software. Then, for the specific drivers go to the next page of the guide 'Using with Arduino IDE.' There is also an arrow at the end of the page that will take you to it. Make sure to go through the setup **step by step** to the end of each page.  

First step in downloading the drivers:  
  
Note: this address needs to be added to your preferences on the Arduino IDE for the Adafruit drivers to appear in your boards manager.

**Note: The main board uses the same processor as the Adafruit Feather M0 Adalogger. Therefore, the driver for the M0 is required to communicate with the board. The instructions above will guide you through the process.**

#### Step 3: Test communication through an onboard LED (making use of example code)
1. Open the Arduino IDE.
2. Connect the board (micro USB) to your computer (USB).
3. On the Arduino IDE select **Tools** > **Board** > **Adafruit Feather M0**
4. Make sure the **Tools** > **Port** reads '**Adafruit Feather M0**'
   1. If this is not the case (either the computer isn't registering the device, there are multiple instances, etc.) go to the Restarting your board file.
5. Select **File** > **Examples** > **Basics** > **Blink**
   1. Once the 'Blink' file opens, switch any 'LED_BUILTIN' statement for a '26.' Alternatively, open the *mod_Blink.ino* file availble in this repository within the *mod_Blink* folder.
      1. If LED 1 begins to blink, then you have been succesful.
   ```
   Note: 26 is the pin designation for Red LED 1 on the board.
   ```
6. Now that you have succesfully communicated with the board, navigate to specific sensors or the general test code to communicate with other components on the board.

#### Resources:
##### In the Arduino IDE 
- **File** > **Examples** for pre-built code that you can use
- **Help** > **Reference** for function names and descriptions
- **Help** > **Troubleshooting**
##### General
 - [TechFest](https://github.com/practicaltech/TechFest)
 - [Arduino](https://www.arduino.cc/en/Guide/ArduinoUno)
 - [Adafruit lessons](https://learn.adafruit.com/series/learn-arduino)
 - [SparkFun](https://learn.sparkfun.com/tutorials)

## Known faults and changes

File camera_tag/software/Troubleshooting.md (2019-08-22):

Common issues and how to resolve them
==========================================

## 1. Board not recognized on IDE
   1. Restart: with the board connected to your computer. Run a simple program on the IDE such as **Blink_mod,** then click on upload (the arrow on the top left). Then, while the load procedure is goig through **compiling sketch** touch a wire from **Reset** to **Ground** twice in quick succession.
      edit2
 

## 2. Code not uploading 
   1. Board selected: make sure the board selected is the **Adafruit Feather M0**
   

##  
###  
   2. Port: make sure the port with the board is selected   

   
   
## 3. Multiple instances appear of board on same port
   1. Save your file, close all instances of the Arduino IDE and restart the program.
   
## 4. Upload process stuck
   1. Board selection: make sure the correct board is selected (refer to image on 'Port')
   2. Code: your code might have an error, try a sketch you know runs to test if this is actually the problem.
   3. Restart: close all IDE instances and restart.

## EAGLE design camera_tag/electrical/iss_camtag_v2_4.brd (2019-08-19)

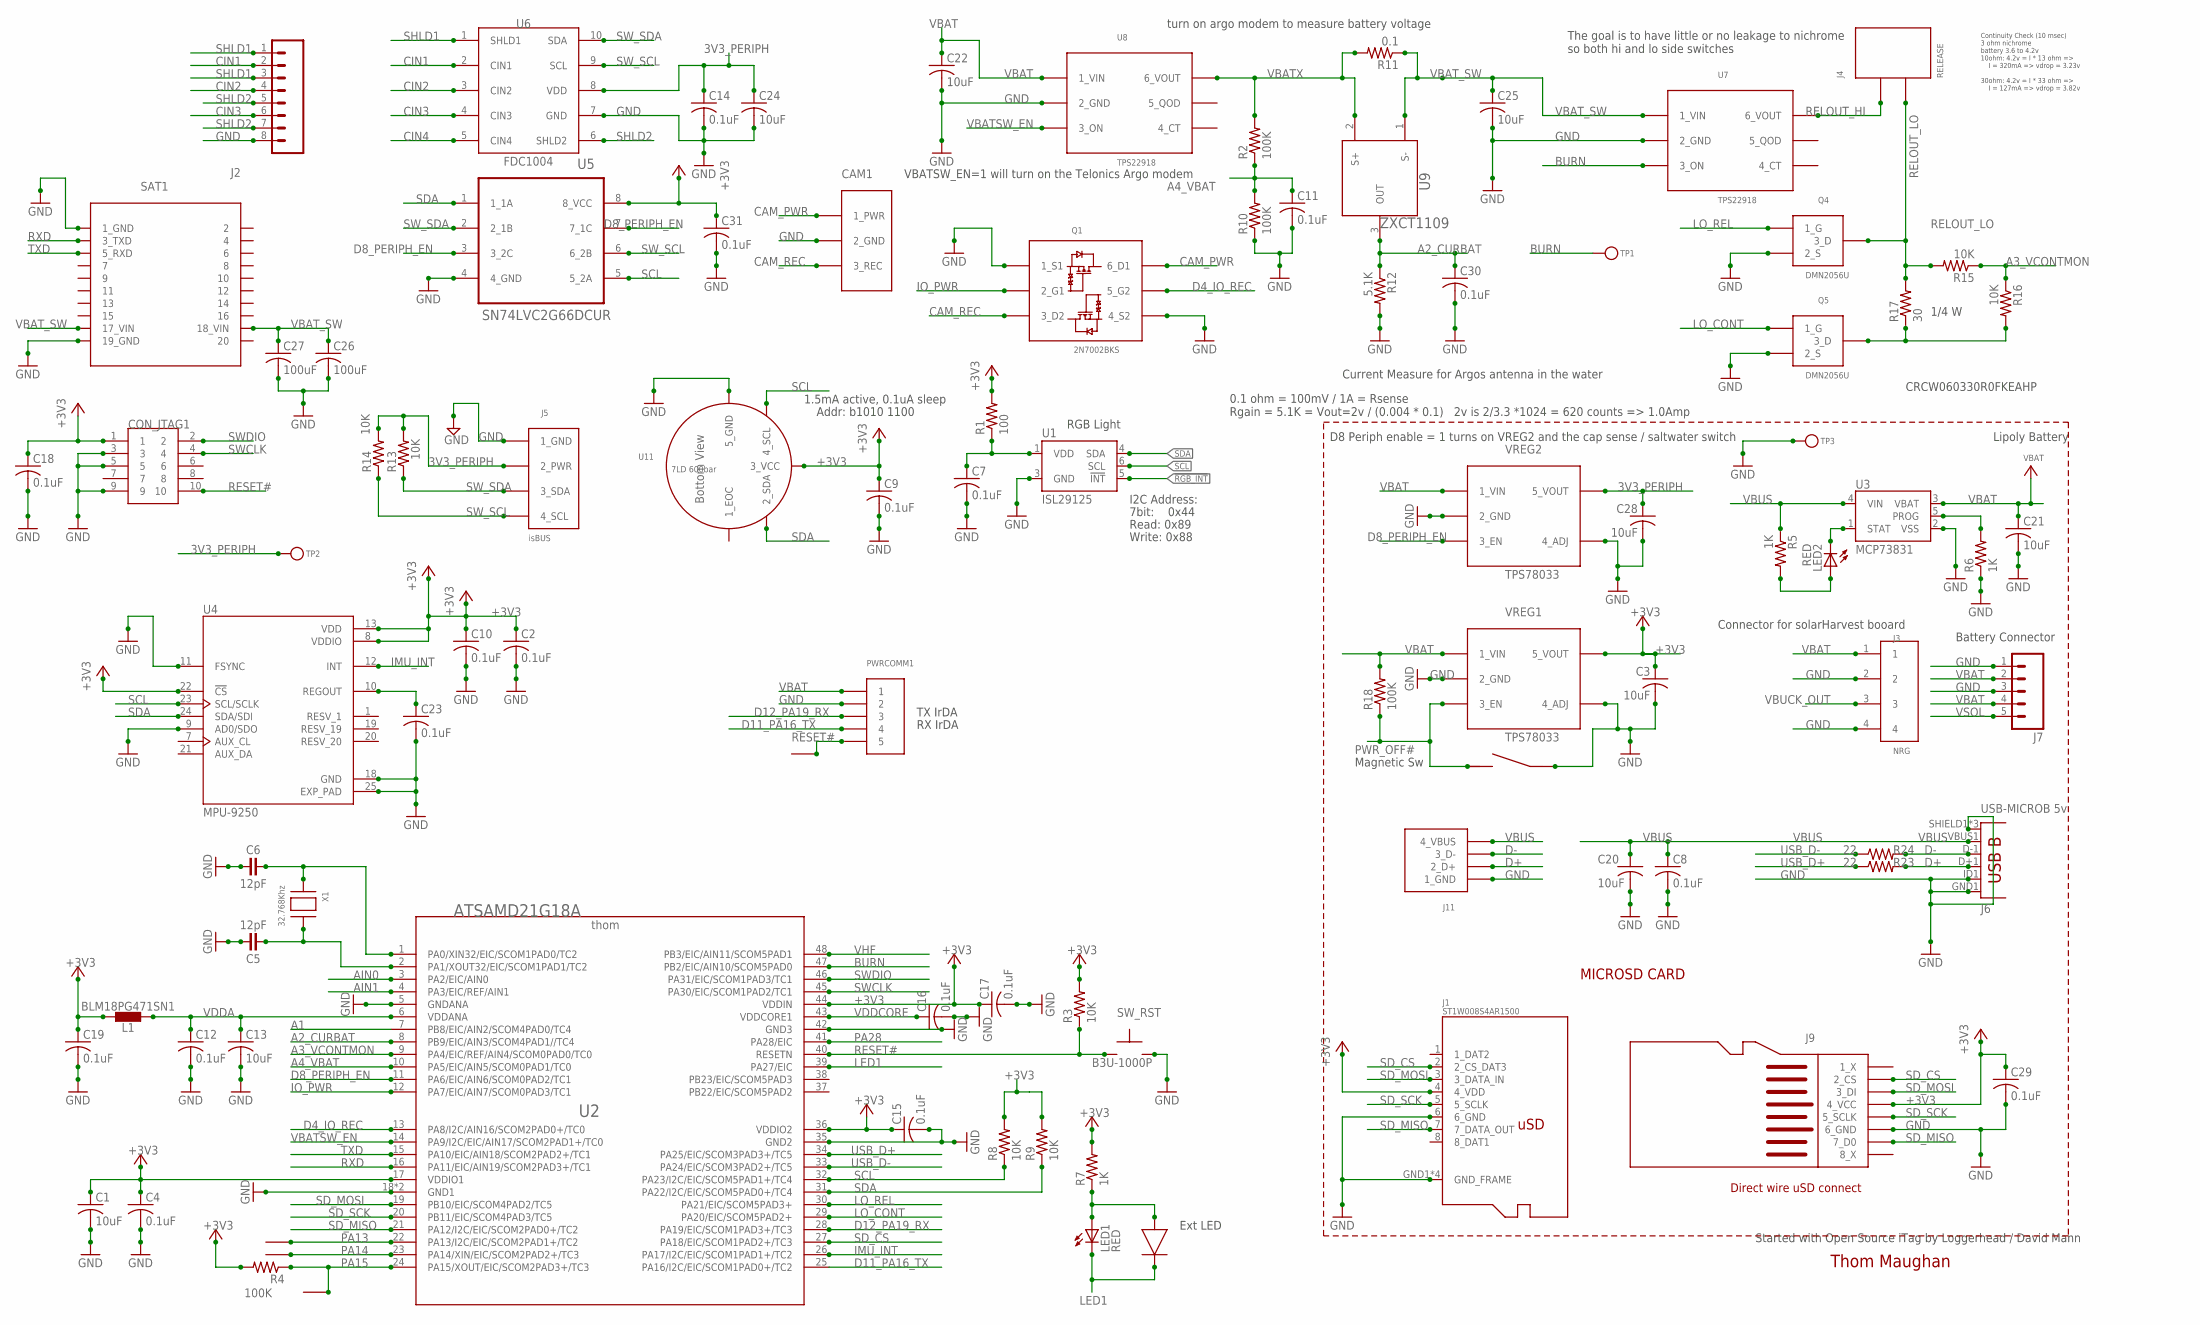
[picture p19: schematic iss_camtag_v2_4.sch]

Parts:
C1, C13, C20, C21, C22, C24, C25: 10uF; C0603
C2, C4, C7, C8, C9, C10, C11, C12, C14, C15, C16, C17, C18, C19, C23, C29, C30, C31: 0.1uF; C0402
C3, C28: 10uF; C0603K
C5, C6: 12pF; C0402
C26, C27: 100uF; C1210
CAM1: CON_1X3_CAMCTRL
CON_JTAG1: HDR-SMT-50MIL/5X2
J1: ST1W008S4AR1500; MICROSD_JAE_ST1W008S4AR1500
J2: CONN_08"; 1X08
J3: NRG; CONNECTOR_1X4_0_1
J4: RELEASE; CON_1X2_0_1
J5: isBUS; CON_1X4_0_1
J6: USB-MICROB 5v; USB-B-MICRO-SMD_V03
J7: M05PTH; 1X05
J9: CON_8_MICROSD_WIRE
J11: CON_1X4_2MM_THRU
L1: BLM18PG471SN1; C0603
LED1, LED2: RED; CHIPLED_0603
PWRCOMM1: CON_1X5_0_1; CONNECTOR_1X5_0_1
Q1: 2N7002BKS; SOT363
Q4, Q5: DMN2056U; SOT23-3
R1: 100; R0402
R2, R4, R10, R18: 100K; R0402
R3, R8, R9, R13, R14, R15, R16: 10K; R0402
R5, R6, R7: 1K; R0402
R11: 0.1; R0603
R12: 5.1K; R0402
R17: 30; R0603
R23, R24: 22; R0402
SAT1: TELONICS-ST-21H2-200A; TELONICS_ST_21H2-200A
SW_RST: B3U-1000P
TP1, TP2, TP3: TESTPOINTROUND1.5MM; TESTPOINT_ROUND_1.5MM
TP4, TP5, TP6: CON_1
U1: ISL29125; ODFN-LD-6
U2: ATSAMD21G18A; TQFN48_7MM
U3: MCP73831; SOT23-5
U4: MPU-9250; MPU-9250-FOOTPRINT
U5: SN74LVC2G66DCUR; ANALOG_SW_SN74LVCG66DCUR
U6: FDC1004; VSSOP-10
U7, U8: TPS22918; SOT23-6
U9: ZXCT1109; SOT23
U11: 7LD 600bar; KELLER_7LD
U$3: CON_2_MAGSW
U$4: CON_2_LED
U$5: CON_1
VREG1, VREG2: TPS78033; SOT23-5
X1: 32.768Khz; XTAL_ABS06

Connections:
3V3_PERIPH: C14.1, C24.1, C28.1, J5.P$2 (2_PWR), R13.2, R14.2, TP2.P$1, U6.8 (VDD), VREG2.P$5 (5_VOUT)
!RGB_INT: U1.5 (!INT)
+3V3: C1.1, C2.1, C3.1, C4.1, C9.1, C10.1, C15.1, C17.1, C18.1, C19.1, C29.1, C31.1, CON_JTAG1.1, J1.4 (4_VDD), J9.4_VCC, J9.P4 (4_VCC), L1.2, R1.2, R3.2, R4.2, R7.2, R8.2, R9.2, U2.17 (VDDIO1), U2.36 (VDDIO2), U2.44 (VDDIN), U4.8 (VDDIO), U4.13 (VDD), U4.22 (!CS), U5.8 (8_VCC), U11.3_VCC, VREG1.P$5 (5_VOUT)
A1: U2.7 (PB8/EIC/AIN2/SCOM4PAD0/TC4)
A2_CURBAT: C30.1, R12.1, U2.8 (PB9/EIC/AIN3/SCOM4PAD1//TC4), U9.3 (OUT)
A3_VCONTMON: R15.1, R16.1, U2.9 (PA4/EIC/REF/AIN4/SCOM0PAD0/TC0)
A4_VBAT: C11.1, R2.1, R10.2, U2.10 (PA5/EIC/AIN5/SCOM0PAD1/TC0)
AIN0: U2.3 (PA2/EIC/AIN0)
AIN1: U2.4 (PA3/EIC/REF/AIN1)
BURN: TP1.P$1, U2.47 (PB2/EIC/AIN10/SCOM5PAD0), U7.3 (3_ON)
CAM_PWR: CAM1.1_PWR, Q1.6 (6_D1)
CAM_REC: CAM1.3_REC, Q1.3 (3_D2)
CIN1: J2.2, U6.2 (CIN1)
CIN2: J2.4, U6.3 (CIN2)
CIN3: J2.6, U6.4 (CIN3)
CIN4: U6.5 (CIN4)
D4_IO_REC: Q1.5 (5_G2), U2.13 (PA8/I2C/AIN16/SCOM2PAD0+/TC0)
D8_PERIPH_EN: U2.11 (PA6/EIC/AIN6/SCOM0PAD2/TC1), U5.3 (3_2C), U5.7 (7_1C), VREG2.P$3 (3_EN)
D11_PA16_TX: PWRCOMM1.4, U2.25 (PA16/I2C/EIC/SCOM1PAD0+/TC2)
D12_PA19_RX: PWRCOMM1.3, U2.28 (PA19/EIC/SCOM1PAD3+/TC3)
D+: J6.D+1 (D+), J11.P$2 (2_D+), R23.2
D-: J6.D-1 (D-), J11.P$3 (3_D-), R24.2
GND: C1.2, C2.2, C3.2, C4.2, C5.2, C6.1, C7.2, C8.2, C9.2, C10.2, C11.2, C12.2, C13.2, C14.2, C15.2, C16.2, C17.2, C18.2, C19.2, C20.2, C21.2, C22.2, C23.2, C24.2, C25.2, C26.2, C27.2, C28.2, C29.2, C30.2, C31.2, CAM1.2_GND, CON_JTAG1.3, CON_JTAG1.5, CON_JTAG1.9, J1.6 (6_GND), J1.GND1 (GND_FRAME), J1.GND2 (GND_FRAME), J1.GND3 (GND_FRAME), J1.GND4 (GND_FRAME), J2.8, J3.2, J3.4, J5.P$1 (1_GND), J6.GND1 (GND), J6.ID1 (USBID), J6.SHIELD1 (SHIELD), J6.SHIELD2 (SHIELD), J6.SHIELD3 (SHIELD), J7.1, J7.3, J9.6_GND, J9.P6 (6_GND), J11.P$1 (1_GND), PWRCOMM1.2, Q1.1 (1_S1), Q1.4 (4_S2), Q4.2 (2_S), Q5.2 (2_S), R6.1, R10.1, R12.2, SAT1.1 (1_GND), SAT1.19 (19_GND), SAT1.21 (1_GND), SAT1.39 (19_GND), SW_RST.P$2, TP3.P$1, U1.3 (GND), U2.5 (GNDANA), U2.18 (GND1), U2.35 (GND2), U2.42 (GND3), U2.THERMAL (GND1), U3.2 (VSS), U4.9 (AD0/SDO), U4.11 (FSYNC), U4.18 (GND), U4.25 (EXP_PAD), U5.4 (4_GND), U6.7 (GND), U7.2 (2_GND), U8.2 (2_GND), U11.5_GND, U$3.2, VREG1.P$2 (2_GND), VREG1.P$4 (4_ADJ), VREG2.P$2 (2_GND), VREG2.P$4 (4_ADJ)
IMU_INT: U2.26 (PA17/I2C/EIC/SCOM1PAD1+/TC2), U4.12 (INT)
IO_PWR: Q1.2 (2_G1), U2.12 (PA7/EIC/AIN7/SCOM0PAD3/TC1)
LAN: LED1.A, R7.1, U$4.P$1 (1A)
LED1: LED1.C, U2.39 (PA27/EIC), U$4.P$2 (2K)
LO_CONT: Q5.1 (1_G), U2.29 (PA20/EIC/SCOM5PAD2+)
LO_REL: Q4.1 (1_G), U2.30 (PA21/EIC/SCOM5PAD3+)
unnamed: C6.2, U2.1 (PA0/XIN32/EIC/SCOM1PAD0/TC2), X1.P$1
unnamed: LED2.C, U3.1 (STAT)
unnamed: LED2.A, R5.2
unnamed: R6.2, U3.5 (PROG)
unnamed: C7.1, R1.1, U1.1 (VDD)
unnamed: C5.1, U2.2 (PA1/XOUT32/EIC/SCOM1PAD1/TC2), X1.P$2
unnamed: Q5.3 (3_D), R16.2, R17.1
unnamed: C23.1, U4.10 (REGOUT)
PA13: TP4.P$1, U2.22 (PA13/I2C/EIC/SCOM2PAD1+/TC2)
PA14: TP5.P$1, U2.23 (PA14/XIN/EIC/SCOM2PAD2+/TC3)
PA15: R4.1, TP6.P$1, U2.24 (PA15/XOUT/EIC/SCOM2PAD3+/TC3)
PA28: U2.41 (PA28/EIC)
PWR_OFF#: R18.1, U$3.1, VREG1.P$3 (3_EN)
RELOUT_HI: J4.P$1, U7.6 (6_VOUT)
RELOUT_LO: J4.P$2, Q4.3 (3_D), R15.2, R17.2
RESET#: CON_JTAG1.10, PWRCOMM1.5, R3.1, SW_RST.P$1, U2.40 (RESETN), U$5.P$1
RXD: SAT1.3 (3_TXD), SAT1.23 (3_TXD), U2.16 (PA11/EIC/AIN19/SCOM2PAD3+/TC1)
SCL: R8.1, U1.6 (SCL), U2.32 (PA23/I2C/EIC/SCOM5PAD1+/TC4), U4.23 (SCL/SCLK), U5.5 (5_2A), U11.4_SCL
SDA: R9.1, U1.4 (SDA), U2.31 (PA22/I2C/EIC/SCOM5PAD0+/TC4), U4.24 (SDA/SDI), U5.1 (1_1A), U11.2_SDA
SD_CS: J1.2 (2_CS_DAT3), J9.2_CS, J9.P2 (2_CS), U2.27 (PA18/EIC/SCOM1PAD2+/TC3)
SD_MISO: J1.7 (7_DATA_OUT), J9.7_DO (7_D0), J9.P7 (7_D0), U2.21 (PA12/I2C/EIC/SCOM2PAD0+/TC2)
SD_MOSI: J1.3 (3_DATA_IN), J9.3_DI, J9.P3 (3_DI), U2.19 (PB10/EIC/SCOM4PAD2/TC5)
SD_SCK: J1.5 (5_SCLK), J9.5_SCK (5_SCLK), J9.P5 (5_SCLK), U2.20 (PB11/EIC/SCOM4PAD3/TC5)
SHLD1: J2.1, J2.3, U6.1 (SHLD1)
SHLD2: J2.5, J2.7, U6.6 (SHLD2)
SWCLK: CON_JTAG1.4, U2.45 (PA30/EIC/SCOM1PAD2/TC1)
SWDIO: CON_JTAG1.2, U2.46 (PA31/EIC/SCOM1PAD3/TC1)
SW_SCL: J5.P$4 (4_SCL), R14.1, U5.6 (6_2B), U6.9 (SCL)
SW_SDA: J5.P$3 (3_SDA), R13.1, U5.2 (2_1B), U6.10 (SDA)
TXD: SAT1.5 (5_RXD), SAT1.25 (5_RXD), U2.15 (PA10/EIC/AIN18/SCOM2PAD2+/TC1)
USB_D+: R23.1, U2.34 (PA25/EIC/SCOM3PAD3+/TC5)
USB_D-: R24.1, U2.33 (PA24/EIC/SCOM3PAD2+/TC5)
VBAT: C21.1, C22.1, J3.1, J7.2, J7.4, PWRCOMM1.1, R18.2, U3.3 (VBAT), U8.1 (1_VIN), VREG1.P$1 (1_VIN), VREG2.P$1 (1_VIN)
VBATSW_EN: U2.14 (PA9/I2C/EIC/AIN17/SCOM2PAD1+/TC0), U8.3 (3_ON)
VBATX: R2.2, R11.2, U8.6 (6_VOUT), U9.2 (S+)
VBAT_SW: C25.1, C26.1, C27.1, R11.1, SAT1.17 (17_VIN), SAT1.18 (18_VIN), SAT1.37 (17_VIN), SAT1.38 (18_VIN), U7.1 (1_VIN), U9.1 (S-)
VBUCK_OUT: J3.3
VBUS: C8.1, C20.1, J6.VBUS1 (VBUS), J11.P$4 (4_VBUS), R5.1, U3.4 (VIN)
VDDA: C12.1, C13.1, L1.1, U2.6 (VDDANA)
VDDCORE: C16.1, U2.43 (VDDCORE1)
VHF: U2.48 (PB3/EIC/AIN11/SCOM5PAD1)
VSOL: J7.5

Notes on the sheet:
MICROSD CARD
7bit: 0x44
I2C Address:
Read: 0x89
Write: 0x88
Addr: b1010 1100
Lipoly Battery
RGB Light
turn on argo modem to measure battery voltage
Continuity Check (10 msec) 3 ohm nichrome battery 3.6 to 4.2v 10ohm: 4.2v = I * 13 ohm => I = 320mA => vdrop = 3.23v 30ohm: 4.2v = I * 33 ohm => I = 127mA => vdrop = 3.82v
The goal is to have little or no leakage to nichrome so both hi and lo side switches
CRCW060330R0FKEAHP
1/4 W
1.5mA active, 0.1uA sleep
Connector for solarHarvest booard
Battery Connector
Thom Maughan
Direct wire uSD connect
VBATSW_EN=1 will turn on the Telonics Argo modem
Magnetic Sw
0.1 ohm = 100mV / 1A = Rsense Rgain = 5.1K = Vout=2v / (0.004 * 0.1) 2v is 2/3.3 *1024 = 620 counts => 1.0Amp
Started with Open Source iTag by Loggerhead / David Mann
Current Measure for Argos antenna in the water
D8 Periph enable = 1 turns on VREG2 and the cap sense / saltwater switch
TX IrDA
RX IrDA
Ext LED

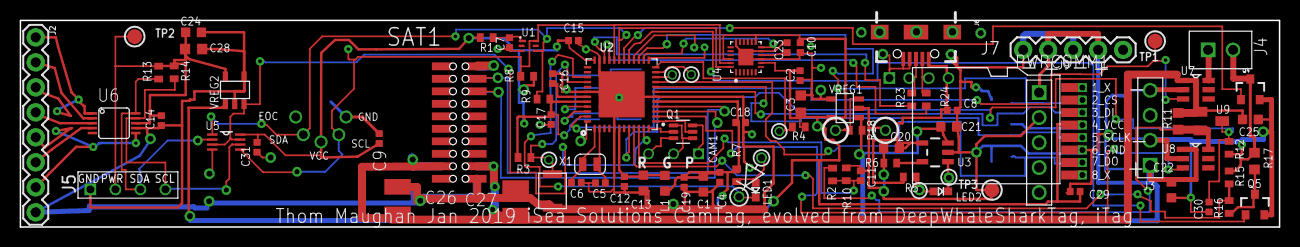
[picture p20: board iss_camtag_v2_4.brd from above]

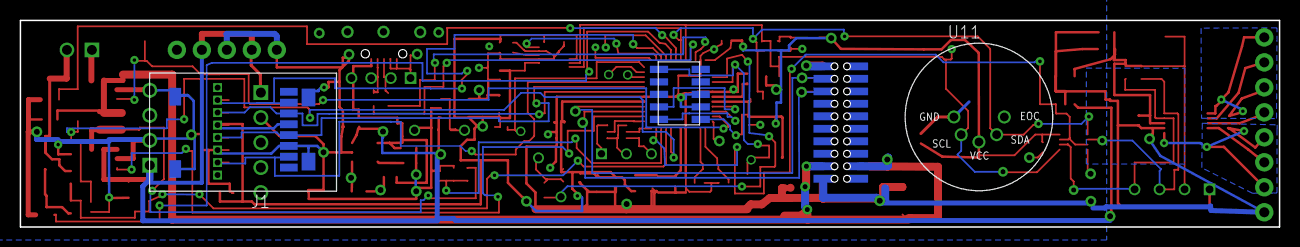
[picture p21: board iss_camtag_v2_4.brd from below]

Board: 4 copper layers, 128.0 x 21.0 mm, 93 parts (3 on the bottom side), 62 nets.

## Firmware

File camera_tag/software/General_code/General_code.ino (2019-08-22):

#include <SPI.h>    // uSD
#include <SD.h>
#include "wiring_private.h" //pinPeripheral() function for serial2 pin mux
#include <Wire.h>   // i2c
#include "SFE_ISL29125.h"
#include "quaternionFilters.h"
#include "MPU9250.h"
#include "amx32.h"
//#include "LowPower.h"

//style guide
// ALL CAPS names are used for 'defines' - this gives names to numbers.
// define names for the IO pins used, try to use schematic names or something close, 
// make other defines that map those schematic names to something more 'logical' as needed
// in programming practice, these gives a symbolic name for a number and solves the problem
// of 'magic numbers'.  it also makes it so the number can be changed in once place (in 
// the 'define') rather than all of the code.  
// An example is the led on pin 13.   
//


#define BOARDTYPE 1   // 0 means Feather M0, 1 means thomz dwsTag

#if BOARDTYPE == 1
#define LED1            26      //26 //PA27  { PORTA, 27, PIO_TIMER, PIN_ATTR_DIGITAL, No_ADC_Channel, NOT_ON_PWM, NOT_ON_TIMER, EXTERNAL_INT_15 }, // p39 previously TX LED
#define D10_SD_CS       10      //10 //PA18 { PORTA, 18, PIO_TIMER, (PIN_ATTR_DIGITAL|PIN_ATTR_PWM|PIN_ATTR_TIMER), No_ADC_Channel, PWM3_CH0, TC3_CH0, EXTERNAL_INT_2 }, // p27
#define A2_CURBAT       16      //16 //PB9 { PORTB,  9, PIO_ANALOG, (PIN_ATTR_PWM|PIN_ATTR_TIMER), ADC_Channel3, PWM4_CH1, TC4_CH1, EXTERNAL_INT_9 }, // p8
#define A4_VBAT         18      //18 //PA5 { PORTA,  5, PIO_ANALOG, (PIN_ATTR_PWM|PIN_ATTR_TIMER), ADC_Channel5, PWM0_CH1, TCC0_CH1, EXTERNAL_INT_5 }, // p10
#define D8_PERIPH_VREG_EN  8     //8  //PA6  { PORTA,  6, PIO_ANALOG, (PIN_ATTR_PWM|PIN_ATTR_TIMER), ADC_Channel6, PWM1_CH0, TCC1_CH0, EXTERNAL_INT_6 }, // p11
#define D9_IO_PWR       9       //9  //PA7  { PORTA,  7, PIO_ANALOG, (PIN_ATTR_PWM|PIN_ATTR_TIMER), ADC_Channel7, PWM1_CH1, TCC1_CH1, EXTERNAL_INT_7 }, // p12
#define D4_IO_REC       4       //4 //PA8  { PORTA,  8, PIO_TIMER, (PIN_ATTR_DIGITAL|PIN_ATTR_PWM|PIN_ATTR_TIMER), ADC_Channel16, PWM0_CH0, TCC0_CH0, EXTERNAL_INT_NMI }, // p23
#define VBATSW_EN       3       //3  //PA9  { PORTA,  9, PIO_TIMER, (PIN_ATTR_DIGITAL|PIN_ATTR_PWM|PIN_ATTR_TIMER), ADC_Channel17, PWM0_CH1, TCC0_CH1, EXTERNAL_INT_9 }, // p14
#define LO_CONT         6       //6  //PA20 { PORTA, 20, PIO_TIMER_ALT, (PIN_ATTR_DIGITAL|PIN_ATTR_PWM|PIN_ATTR_TIMER_ALT), No_ADC_Channel, PWM0_CH6, TCC0_CH6, EXTERNAL_INT_4 }, // p29
#define LO_REL          7       //7  //PA21 { PORTA, 21, PIO_TIMER_ALT, (PIN_ATTR_DIGITAL|PIN_ATTR_PWM|PIN_ATTR_TIMER_ALT), No_ADC_Channel, PWM0_CH7, TCC0_CH7, EXTERNAL_INT_5 }, // p30
#define HI_REL          19      //19 //PB2 { PORTB,  2, PIO_ANALOG, 0, ADC_Channel10, NOT_ON_PWM, NOT_ON_TIMER, EXTERNAL_INT_2 }, // p47
#define D13_IMU_INT     13      //13 //PA17 { PORTA, 17, PIO_TIMER, (PIN_ATTR_DIGITAL|PIN_ATTR_PWM|PIN_ATTR_TIMER), No_ADC_Channel, PWM2_CH1, TCC2_CH1, EXTERNAL_INT_1 }, // p26 SCK
#define VCONTMON        17      //V1.8 hardware not routed, 17 //PA4 { PORTA,  4, PIO_ANALOG, (PIN_ATTR_PWM|PIN_ATTR_TIMER), ADC_Channel4, PWM0_CH0, TCC0_CH0, EXTERNAL_INT_4 }, // p9
#define SERCOM1_RX      12      // atsamd21g sercom1 peripheral is mapped to software Serial2 object
#define SERCOM1_TX      11      // atsamd21g sercom1 peripheral

//MPU9250
#define I2Cclock 400000
#define I2Cport Wire
#define MPU9250_ADDRESS MPU9250_ADDRESS_AD0
float imu_srate = 100.0;

//RGB
SFE_ISL29125 RGB_sensor;//RGB sensor 
#define LEDRED      LED1
#define SD_CS       D10_SD_CS
#endif
//-------------------------------

File logfile;

// RX on pin 12 which is portA on the processor PA19, TX on pin 11 PA16
Uart Serial2 (&sercom1, SERCOM1_RX, SERCOM1_TX, SERCOM_RX_PAD_3, UART_TX_PAD_0);

void setup()
{
  gpio_init();            // dswTag or Feather M0 handled here
  Wire.begin();
  //connect at 115200 so we can read the GPS fast enough and echo without dropping chars
  //also spit it out
  Serial.begin(115200);
  //while(!Serial)    {;}

  Serial2.begin(115200);
  // while(!Serial2)    {;}
  
  //Assign pins 12 & 11 SERCOM functionality
  pinPeripheral(SERCOM1_RX, PIO_SERCOM); // Serial2 RX  12
  pinPeripheral(SERCOM1_TX, PIO_SERCOM); // Serial2 TX  11
  delay(2000);

  //see if the card is present and can be initialized:
  if(!SD.begin(SD_CS))
  {
    Serial.println("Card init. failed!");
    error(2);
  }
  char filename[15];
  strcpy(filename, "/ANALOG00.TXT");
  for (uint8_t i = 0; i < 100; i++)
  {
    filename[7] = '0' + i/10;
    filename[8] = '0' + i%10;
//create if does not exist, do not open existing, write, sync after write
    if(! SD.exists(filename))
    {
      break;
    }
  }

  logfile = SD.open(filename, FILE_WRITE);
  if(!logfile)
  {
    Serial.print("Couldnt create ");
    Serial.println(filename);
    error(3);
  }
  Serial.print("Writing to ");
  Serial.println(filename);

  Serial.println("Ready! test1");
}



void gpio_init()
{
#if BOARDTYPE == 0
  pinMode(LEDRED, OUTPUT);    // 13
  pinMode(8, OUTPUT);
#endif

  
#if BOARDTYPE == 1  
    pinMode(D8_PERIPH_VREG_EN, OUTPUT);     //8  //PA6
    digitalWrite(D8_PERIPH_VREG_EN, HIGH);   // voltage regulator for FCD1004 (if left off, causes i2c hang)
    pinMode(VBATSW_EN, OUTPUT);             //3  //PA9
    digitalWrite(VBATSW_EN, LOW);
    pinMode(LED1, OUTPUT);            //26 //PA27// appLed (was ledGreen on iTag, is redLed on dwstag)
    digitalWrite(LED1, LOW);
    pinMode(LO_CONT, OUTPUT);        //6  //PA20  // LO_CONT PA20
    digitalWrite(LO_CONT, LOW);  
    pinMode(LO_REL, OUTPUT);          //7  //PA21
    digitalWrite(LO_REL, LOW);       // LO_REL PA21
    pinMode(HI_REL, OUTPUT);          //19 //PB2
    digitalWrite(HI_REL, LOW);        // aka BURN (burn is used on schematic for iTag compat)

    //new
    pinMode(D10_SD_CS, OUTPUT);     //10 //PA18// used for sd card
    digitalWrite(D10_SD_CS, LOW);
    pinMode(D9_IO_PWR, OUTPUT);   //9  //PA7
    digitalWrite(D9_IO_PWR, LOW);
    pinMode(D4_IO_REC, OUTPUT);          //4 //PA8
    digitalWrite(D4_IO_REC, LOW);

    pinMode(D13_IMU_INT, INPUT);      //13 //PA17   Not used?? 
        
    // PB9, pin 8, A2 is CURBAT  BatteryCurrent
    pinMode(A2_CURBAT, INPUT);
    pinMode(A4_VBAT, INPUT);  
    pinMode(VCONTMON, INPUT);    // A3 //PA4
    pinMode(A4_VBAT, INPUT);        //18 //PA5

     //Test RGB initialization
      if (RGB_sensor.init()){
      Serial.println("Sensor Initialization Successful\n\r");
    }
      else{
        Serial.println("failed RGB");
    }
    ///////////////////////////////////////////////////////
#endif
    
}


// learn about SD card and file read/write at https://www.arduino.cc/en/Reference/SD


uint8_t i=0;
int loopCnt = 0;
void loop()
{
  /////////////////////////////////////////////////////////////////////////////////////////////////////////////
  // Read sensor values (16 bit integers)
  unsigned int red = RGB_sensor.readRed();
  unsigned int green = RGB_sensor.readGreen();
  unsigned int blue = RGB_sensor.readBlue();

  //code for printing out RGB sensor readings
  // Print out readings, change HEX to DEC if you prefer decimal output
  //Serial.print("Red: "); Serial.println(red,DEC);
  //Serial.print("Green: "); Serial.println(green,DEC);
  //Serial.print("Blue: "); Serial.println(blue,DEC);
  //Serial.println();
  //delay(100);
  //code for triggering cam when red light is shined on RGB
  /*if (red > green){
    Serial.println("Takin picture cap'n");
    digitalWrite(D9_IO_PWR, HIGH);
    delay(100);
    digitalWrite(D9_IO_PWR, LOW);
  }
  else{
    Serial.println("Too much blue and green");
  }*/
  /////MPU9250////////MPU9250///////MPU9250//////MPU9250////////
    MPU9250 myIMU0(MPU9250_ADDRESS, I2Cport, I2Cclock);
    MPU9250 myIMU1(MPU9250_ADDRESS, I2Cport, I2Cclock);
    myIMU0.initMPU9250();
//    myIMU0.MPU9250SelfTest(myIMU0.selfTest);
//    Serial.print(F("x-axis self test: acceleration trim within : "));
//    Serial.print(myIMU0.selfTest[0],1); Serial.println("% of factory value");
//    Serial.print(F("y-axis self test: acceleration trim within : "));
//    Serial.print(myIMU0.selfTest[1],1); Serial.println("% of factory value");
//    Serial.print(F("z-axis self test: acceleration trim within : "));
//    Serial.print(myIMU0.selfTest[2],1); Serial.println("% of factory value");
//    Serial.print(F("x-axis self test: gyration trim within : "));
//    Serial.print(myIMU0.selfTest[3],1); Serial.println("% of factory value");
//    Serial.print(F("y-axis self test: gyration trim within : "));
//    Serial.print(myIMU0.selfTest[4],1); Serial.println("% of factory value");
//    Serial.print(F("z-axis self test: gyration trim within : "));
//    Serial.print(myIMU0.selfTest[5],1); Serial.println("% of factory value");
//    delay(1000);
    // Calibrate gyro and accelerometers, load biases in bias registers
    myIMU0.calibrateMPU9250(myIMU0.gyroBias, myIMU0.accelBias);
    myIMU0.readAccelData(myIMU0.accelCount);
    //Serial.println("get REEEEADDDDDY");
    //Serial.print(F("x-axis good good: acceleration : "));
    //Serial.print(myIMU0.accelCount[0],1);
  
  myIMU0.initMPU9250();
  byte c = 0x00;
  byte d = 0x00;
  c = myIMU0.readByte(MPU9250_ADDRESS_AD0, WHO_AM_I_MPU9250);
  d = myIMU1.readByte(MPU9250_ADDRESS_AD1, WHO_AM_I_MPU9250);
  //test comm with MPU
//  Serial.print(F("MPU9250 I AM 0x"));
//  Serial.print(c, HEX);
//  Serial.print(F(" I should be 0x"));
//  Serial.println(0x71, HEX);
//  Serial.print("Received AD0: 0x");
//  Serial.print(c, HEX);
//  Serial.print(", AD1: 0x");
//  Serial.println(d, HEX);
    //read gyro, accel, and magnet
    myIMU0.getAres();
    myIMU0.getGres();
    myIMU0.getMres();
    //accel
    myIMU0.readAccelData(myIMU0.accelCount);
    // This depends on scale being set
    myIMU0.ax = (float)myIMU0.accelCount[0] * myIMU0.aRes; // - myIMU.accelBias[0];
    myIMU0.ay = (float)myIMU0.accelCount[1] * myIMU0.aRes; // - myIMU.accelBias[1];
    myIMU0.az = (float)myIMU0.accelCount[2] * myIMU0.aRes; // - myIMU.accelBias[2];
//    Serial.println(myIMU0.ax);
//    Serial.println(myIMU0.ay);
//    Serial.println(myIMU0.az);
    
    //Gyro
    myIMU0.readGyroData(myIMU0.gyroCount);  // Read the x/y/z adc values
    // Calculate the gyro value into actual degrees per second
    // This depends on scale being set
    myIMU0.gx = (float)myIMU0.gyroCount[0] * myIMU0.gRes;
    myIMU0.gy = (float)myIMU0.gyroCount[1] * myIMU0.gRes;
    myIMU0.gz = (float)myIMU0.gyroCount[2] * myIMU0.gRes;
//    Serial.println(myIMU0.gx);
//    Serial.println(myIMU0.gy);
//    Serial.println(myIMU0.gz);

    //magnetometer
    myIMU0.readMagData(myIMU0.magCount);  // Read the x/y/z adc values
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

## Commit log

2019-08-05 Create Board_design
2019-08-23 Delete Hot_Glue_Camera.jpg
    Updated the picture to outline the flex wires with purple boxes.

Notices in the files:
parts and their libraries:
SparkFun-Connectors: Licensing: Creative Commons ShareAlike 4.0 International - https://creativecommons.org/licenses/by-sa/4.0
